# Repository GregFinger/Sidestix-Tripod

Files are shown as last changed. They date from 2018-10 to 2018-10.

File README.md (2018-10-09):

# Sidestix-Tripod

## NOTE: This is currently a work-in-progress

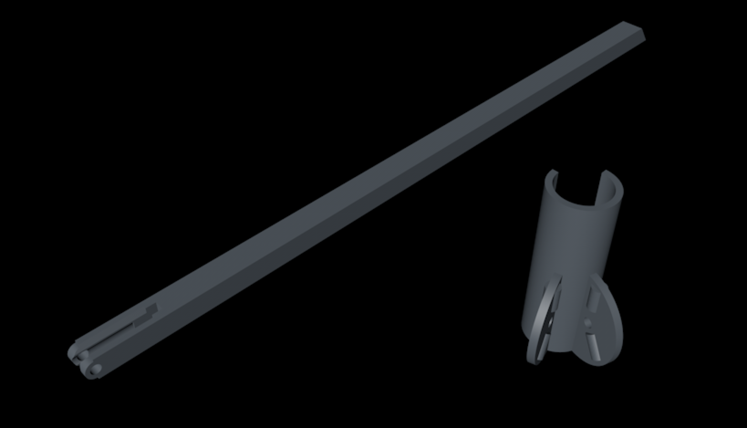
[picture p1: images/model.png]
model pic


Cinema4D and STL files provided for modification and 3D printing purposes. They can be found in the [models folder](https://github.com/GregFinger/Sidestix-Tripod/tree/master/models).

This consists of two parts, the clip and the legs. The clip has two arc-shaped wings that extend from the clip. Each wing has two small rounded ridges that serve as detents to secure the leg in two positions: retracted and tripod. Retracted means the legs are parallel with the crutch and sit flush against the shaft. Tripod means the legs are in the lowered position and act as two extra feet and assist the crutch with standing upright.

My most recent tests with 3D printing have been with a Creality CR-10S S4 printer, using PLA material and 50% infill (to give the tripod more weight).

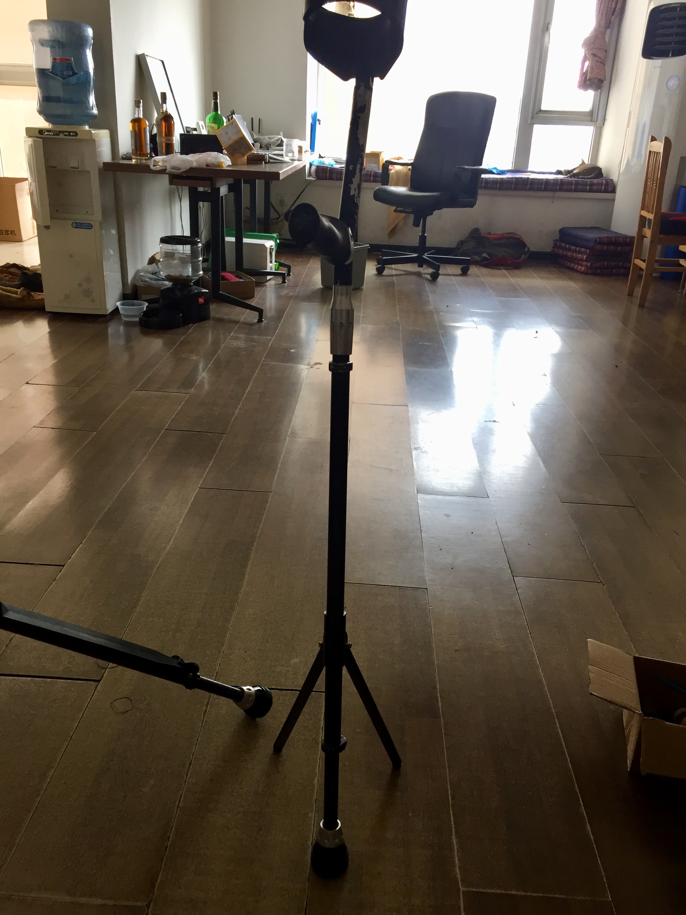
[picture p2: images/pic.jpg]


### Instructions

M4 bolts and nuts are needed to secure the leg to the clip. The clip should be attached to the lower end of the crutch shaft and 180° directly behind the grip handle is the best. It will take a little force to attach the clip to the crutch. Rubber feet can be glued to the end of the legs for better traction with the ground. Strong glue is recommended. Once attached, the legs can be swivelled between the two positions: retracted and tripod.

In the picture above, the crutch in the middle is in the tripod position. Off to the left side, you can see the other crutch with the legs folded up in the retracted position.

### Notes for Improvements

* The detent system needs some work. The positions are fine, but the leg does not stay solidly secure. The place where the leg splits, for the pivot point, bulges out especially when over one of the detent ridges. The makes for a loose fit on the ridge. It also eventually contributes to the leg getting a permanent deformation on the pivot point, rendering it useless.

* A M4 bolt fits perfectly in the hole of the clip's wing, but for some reason it's snug with the hole in the leg's pivot point. This is an easy modification, just make the hole slightly larger in the model file.

* The M4 bolt is also a bit difficult because the space between the wings (55° angle) is too small to insert the bolts from the middle. If you insert them from the outside, then the space between is too small to fit the M4 nuts in there.

* The clip seems to loosen up over time. It initially is very tight, but seems to loosen up and becomes too easy to slide along the crutch,

* The material used for printing (and even the printing method itself) could be improved. I'm currently using a FBM style printer with PLA material. Both of these are entry level in the realm of 3D printing and should not be used in a professional/commercial environment. Using better materials and better methods might solve some of the above problems.

### Potential Future Modifications

* A trigger system, maybe attached to the handle, so the user doesn't manually have to change the leg between detent positions. 

* A  method where the clip can lock onto the best position along the crutch. Currently trying to get directly 180° behind the grip handle is not easy or convenient.

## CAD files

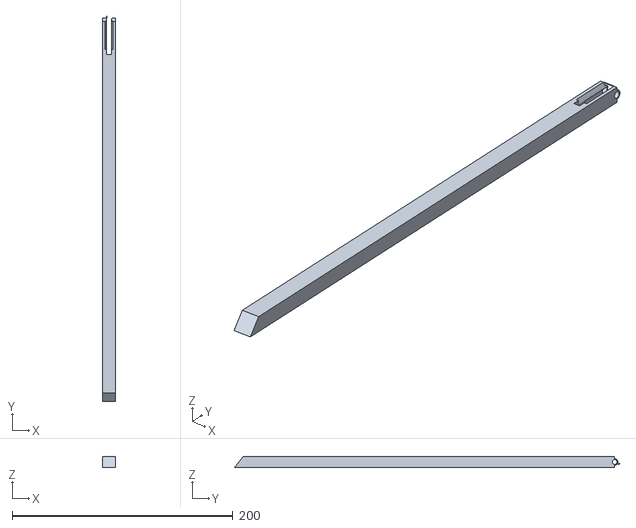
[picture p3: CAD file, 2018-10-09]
models/leg.stl
12.0 x 349.0 x 10.0

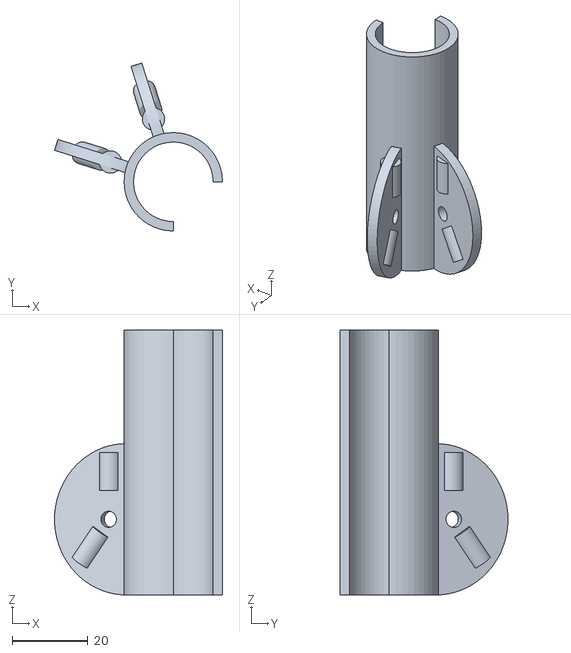
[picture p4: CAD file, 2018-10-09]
models/clip.stl
44.4 x 44.4 x 70.0
